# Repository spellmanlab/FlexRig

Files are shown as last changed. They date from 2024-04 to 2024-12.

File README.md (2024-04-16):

# FlexRig


FlexRig is an open-source platform for head-fixed mouse behavior. Originally designed to run an attentional set-shifting task, it can be used for a wide range of water reward-based tasks involving auditory, whisker somatosensory, and/or olfactory stimuli.

To start using FlexRig:
1. Download the repository
2. Gather the components from the parts list. This includes url-links to commercially available items, 3D-printable .stl files, CNC-machinable files, and printable PCB board design 
4. Assemble the rig, following the illustrated assembly guide
5. Install the Arduino function library

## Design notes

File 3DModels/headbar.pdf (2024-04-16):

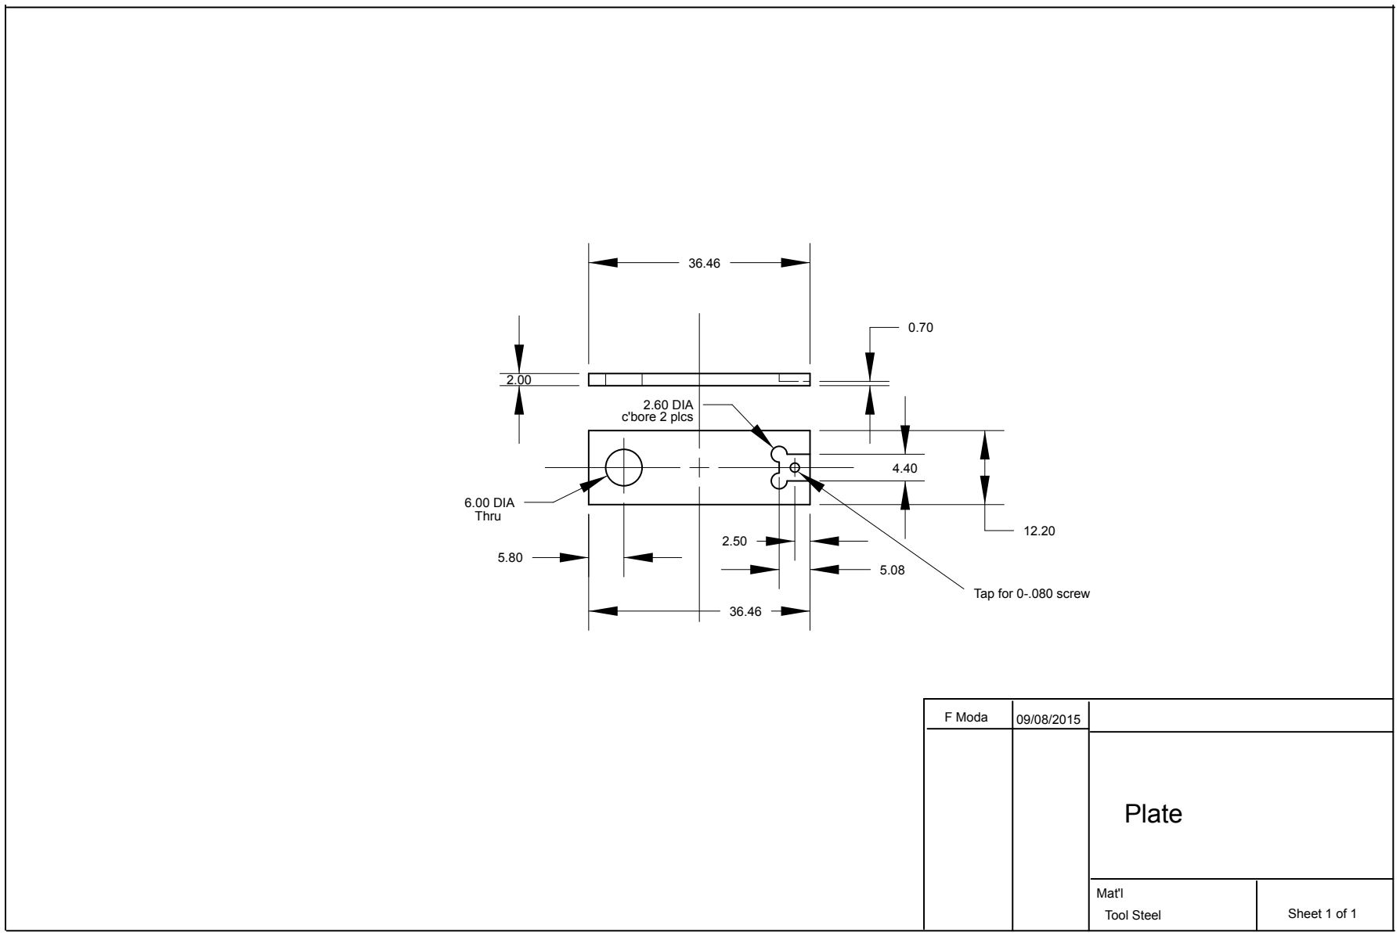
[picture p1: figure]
F Moda; Mat'l; Sheet 1 of 1; 6.00 DIA; 2.60 DIA c'bore 2 plcs; Thru; Tool Steel; Plate; Tap for 0-.080 screw

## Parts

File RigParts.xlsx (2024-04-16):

part # | component | item description | # | usage notes | part ID | supplier | link
P1 | base + head restraint | 6"x6" breadboard | 1 | platform for all components | MB6 | Thorlabs | https://www.thorlabs.com/thorproduct.cfm?partnumber=MB6
P2 |  | 3" x 1/2" posts | 2 | supports head plates | TR3 | Thorlabs | https://www.thorlabs.com/thorproduct.cfm?partnumber=TR3
P3 |  | adhesive teflon sheet, Teflon (PTFE) sheets, various sizes, 0.03" (1/32") thick, with 3M 300LSE industrial-strength self-adhesive backing [TEFLON-3M-all] | 1 | covers the base, makes for easier cleanup | 3M | 3M | https://www.amazon.com/Teflon-industrial-strength-self-adhesive-backing-TEFLON12x12-3M/dp/B00CM06JAG
P4 |  | Adapter with Internal 4-40 Threads and External 1/4"-20 Threads | 2 | mounting arduino to base | AE4E25E | Thorlabs | https://www.thorlabs.com/thorproduct.cfm?partnumber=AE4E25E#ad-image-0
P5 |  | 1/4"-20 set screw, length 0.5" | 1 | slotting treadmill front | 91375A537 | McMaster-Carr | https://www.mcmaster.com/91375A537/
P6 |  | 1/4"-20 cap screw, length 0.5-1" | 3 | slott treadmill, rear, fastening air/water holder to base | 92220A183 | McMaster-Carr | https://www.mcmaster.com/92220A183/
P7 |  | button-head screw | 1 | hold Arudino case to base | 92949A110 | McMaster-Carr | https://www.mcmaster.com/92949A110/
P8 |  | 4-40 cap screw, 1" length | 1 | hold Arduino to case and base | 91251A110 | McMaster-Carr | https://www.mcmaster.com/91251A110/
P9 |  | head bars | 2 | fastens head plate to head posts | headbar.stl |  | https://github.com/spellmanlab/FlexRig
P10 |  | Arduino Mega 2560 | 1 | control components and log behavior data | 1050-1018-ND | Digikey | https://www.digikey.com/en/products/detail/arduino/A000067/2639006
P11 | air/water control | flowmeter, Masterflex Variable-Area Flowmeter with Valve, Acrylic Housing, Brass Fitting, 50-mm; 0.5 LPM Air | 1 | regulates airflow to odorants | 2968K201 | McMaster-Carr | https://www.mcmaster.com/2968K201/
P12 |  | M5 screw | 1 | secures flow meter to holder | 92290A277 | McMaster-Carr | https://www.mcmaster.com/92290A277/
P13 |  | Luer 3-way stopcock, F/F/M | 2 | air and water intake | PVAP-MFF-PC | ISM | https://www.industrialspec.com/shop/pvap-mff-pc.html
P14 |  | Luer 3-way T splitter, F/F/M | 5 | coupled to water and odorant bottles | CFFT-WN | ISM | https://www.industrialspec.com/shop/plastic-fittings/plastic-luer-fittings/luer-to-luer-plastic-luer-fittings/cfft-series/cfft-wn.html
P15 |  | Luer 3/32" barbed connector, F | 1 | connects water bottle to water intake stopcock | CFLLA-332-N | ISM | https://www.industrialspec.com/shop/plastic-fittings/plastic-luer-fittings/luer-to-barb-plastic-luer-fittings/cfla-series/cflla-332-n.html
P16 |  | Luer 3/32" barbed connector, M | 2 | 1) connects air intake to flowmeter, 2) connects water intake to water solenoids | CIML-332EA-WN | ISM | https://www.industrialspec.com/shop/plastic-fittings/plastic-luer-fittings/luer-to-barb-plastic-luer-fittings/ciml-series/ciml-332ea-wn.html
P17 |  | Luer elbow adaptor, M-F | 3 | 1) connects water bottle to water intake, 2-3) couple to lickspout needles | CFLET-WN | ISM | https://www.industrialspec.com/shop/plastic-fittings/plastic-luer-fittings/luer-to-luer-plastic-luer-fittings/cfle-series/cflet-wn.html
P18 |  | Luer snap-on threads | 8 | secure male luer adapters to female luer adapters | CLFSR-WN | ISM | https://www.industrialspec.com/shop/plastic-fittings/plastic-luer-fittings/panel-mount-luers/clfsr-series-finger-snap-luer-lock-ring/clfsr-wn.html
P19 |  | 1/8 NPT fitting (3/32" barb) | 2 | connecting 1/16" PTFE tubing to flowmeter intake and exhaust | F325483 | ISM | https://www.industrialspec.com/shop/f325483.html
P20 |  | PTFE (Teflon) tubing, 1/16" OD, 1/32" ID | 100' | air and water lines | PTFE-132116-100 | ISM | https://www.industrialspec.com/shop/plastic-tubing/ptfe-fluoropolymer-tubing/ptfe-132116-100.html
P21 |  | Luer 3/32" barbed check valve, intake | 4 | air intake to odorant tube | BCV-67220-ML | ISM | https://www.industrialspec.com/shop/medical-products/medical-check-valves/bcv-67220-ml.html
P22 |  | Luer 3/32" barbed check valve, exhaust | 4 | air exhaust from odorant tube | BCV-67FL-220 | ISM | https://www.industrialspec.com/shop/medical-products/medical-check-valves/bcv-67fl-220.html
P23 |  | 6-40 threaded ferrules | 24 | coupling to for 1/16" OD tubing | SKU 640FF-16 | Globalfia | https://www.globalfia.com/shop/6-40-Fittings-p460224016
P24 |  | 1/4 OZ luer-capped dispensing bottles | 4 | contains odorants | JG0.25BC | Jensen Global | https://jensenglobal.com/products/0-25-ounce-cylinder-bottle-cap-kit
P25 |  | 2 OZ luer-capped dispensing bottle | 1 | contains water | JG2.0BC Bl2 | Jensen Global | https://jensenglobal.com/collections/boston-round-bottle-and-cap/products/boston-round-bottles-caps-1-2-ounces
P26 |  | Silicon tubing, 1/32" I.D., 5/32" O.D. | 10' | coupling 1/16" PTFE tubing to barbs | 57286 | US Plastics | https://www.usplastic.com/catalog/item.aspx?itemid=31559&v1=&v7=&gad_source=1
P27 |  | Silicon tubing, 1/16" I.D., 1/8" O.D. |  | coupling 1/16" PTFE tubing to male Luer connectors at odorant bottles | 57287 | US Plastics | https://www.usplastic.com/catalog/item.aspx?itemid=31560&clickid=related-slider
P28 |  | air/water holder | 1 | holds flowmeter, water bottle, odorant bottles and luer connectors | airWaterHolder.stl |  | https://github.com/spellmanlab/FlexRig
P29 |  | odorant manifold | 1 | merges odorant exhaust channels | threadedManifold.emsx |  | https://github.com/spellmanlab/FlexRig
P30 | lick stage | gavage needle, 20g | 2 |  | AFN2025S | GavageNeedle | https://gavageneedle.com/products/reusable-oral-gavage-needle?variant=865840675
P31 |  | translating post | 1 | hold lick ports | BTP2.0 (https://www.newport.com/p/BTP2.0) | Newport | https://www.newport.com/f/0.5-in.-translating-optical-posts
P32 |  | xy translating stage | 1 | hold lick ports | M-MT-XY | Newport | https://www.newport.com/p/M-MT-XY
P33 |  | 6-40 machine | 2 | hold odorant tube | 94812A663 | McMaster-Carr | https://www.mcmaster.com/94812A663/
P34 |  | 6-40 threaded ferrules | 1 | coupling to for 1/16" OD tubing | SKU 640FF-16 | Globalfia | https://www.globalfia.com/shop/6-40-Fittings-p460224016
P35 |  | plastic 8/32" thumb screw | 1 | securing lickspouts to holder | 94320A393 | McMaster-Carr | https://www.mcmaster.com/94320A393/
P36 |  | 2-56" x 5/8" screw | 1 | securing translating post to holder | 91802A083 | McMaster-Carr | https://www.mcmaster.com/91802A083/
P37 |  | 2-56 nut | 1 | securing translating post to holder | 90480A003 | McMaster-Carr | https://www.mcmaster.com/90480A003/
P38 |  | lickspout holder | 1 | securing lickspouts to xy stage and base | lickSpoutPostHolder.stl |  | https://github.com/spellmanlab/FlexRig
P39 |  | 8-32 cap screw, 1/4" length | 3 | 1) fastening lickspout holder to XY stage, 2) fastening head bars to posts | 90128A191 | McMaster-Carr | https://www.mcmaster.com/90128A191/
P40 | treadmill | toy tank treads | 76 links | supports mouse, facilitates running, conducts lick detection current | TT35056 | Warp United | https://www.amazon.com/Assembled-Workable-T-34-76-T-34-85-Self-propelled/dp/B07Q9QJSNC
P41 |  | steel bearings | 6 | treadmill axle bearings | 7804K143 | McMaster-Carr | https://www.mcmaster.com/7804K143/
P42 |  | 2" mini posts | 2 | treadmill axles | MS2R | Thorlabs | https://www.thorlabs.com/thorproduct.cfm?partnumber=MS2R
P43 |  | 4-40 screws and washers | 1 kit | securing bearings to treadmill frame | ALAST0440 | Fastener Express | https://www.fastener-express.com/4-40-alloy-stainless-asortment.aspx
P44 |  | rotary encoder | 1 | measure running speed | AMT103-V | Digi-key | https://www.digikey.com/en/products/detail/cui-devices/AMT103-V/827016?s=N4IgTCBcDaIIIFkAqBGADAZgLQDUQF0BfIA
P45 |  | 1/4-20 cap screws, 1/2" | 4 | secure treadmill to breadboard | 92220A183 | McMaster-Carr | https://www.mcmaster.com/92220A183/
P46 |  | 3mm banana plug | 1 | 3.3v lick detection voltage connector (post to mouse platform) | generic | Amazon | https://www.amazon.com/LinsyRC-Gold-Plated-Connector-Adapter-Battery/dp/B08H8MY431
P47 |  | mouse platform | 1 | supports mouse/treadmill | treadmillBase.stl |  | https://github.com/spellmanlab/FlexRig
P48 |  | treadmill sprockets (aluminum) | 2 | holds treads | treadmillSprockets.stl |  | https://github.com/spellmanlab/FlexRig
P49 | command stage | 2-way solenoid valves, 12v, face-mounted | 2 | solenoid valves for dispensing water reward | LHDB1252115H | The Lee Company | https://www.theleeco.com/resources/files/2-port-hdi-solenoid-valve-pds-124-2014-12/
P50 |  | 3-way solenoid valves, 12v, face-mounted | 4 | route air to one of the four odorant tubes or bypass all four | LHDA1221411H | The Lee Company | https://www.theleeco.com/products/electro-fluidic-systems/solenoid-valves/control-valves/lhd-series/3-port/face-mount/
P51 |  | air/water face-mount manifold (aluminum) | 1 | mount solenoids to tubing | threadedFaceMount.emsx |  | https://github.com/spellmanlab/FlexRig
P52 |  | solenoid retention brackets | 3 | attaches selonoids to face mount manifolds (optional) | LLWX0307130A | The Lee Company | https://www.theleeco.com/products/electro-fluidic-systems/solenoid-valves/control-valves/general-accessories-replacement-parts/
P53 |  | 2-56 solenoid retention screws, 0.5" length | 8 | fasten solenoids to face mount | 91251A081 | McMaster-Carr | https://www.mcmaster.com/91251A081/
P54 |  | DF Robot DF Player Pro | 1 | sound card | 1738-DFR0768-ND | Digikey | https://www.digikey.com/en/products/detail/dfrobot/DFR0768/13978502
P55 |  | H-bridge | 2 | 4-40 cap screw, 1" length |  |  | https://www.digikey.com/en/products/detail/texas-instruments/SN754410NE/380180?gad_source=1
P56 |  | 6-pin screw terminal, 2.54mm pitch | 2 | connecting wires to PCB board | A98337-ND | Digikey | https://www.digikey.com/en/products/detail/te-connectivity-amp-connectors/282834-6/1153267?gad_source=1
P57 |  | 2-pin screw terminal, 2.54mm pitch | 1 | connecting linear actuator to PCB board | A98333-ND | Digikey | https://www.digikey.com/en/products/detail/te-connectivity-amp-connectors/282834-2/1150135?gad_source=1
P58 |  | 8-pin male header | 6 | connecting PCB board to arduino | 732-5321-ND | Digikey | https://www.digikey.sk/en/products/detail/w%C3%BCrth-elektronik/61300811121/4846839
P59 |  | 2-pin female header | 6 | connecting solenoids to board | 2057-RS1-02-G-ND | Digikey | https://www.digikey.com/en/products/detail/adam-tech/RS1-02-G/9832044
P60 |  | 6-pin female header | 2 | connecting sound board to main board | 2057-RS1-06-G-ND | Digikey | https://www.digikey.com/en/products/detail/adam-tech/RS1-06-G/9832050
P61 |  | 2x18 pin stackable female header | 1 | connecting PCB board to Arduino | SSW-118-03-G-D-ND | Digikey | https://www.digikey.com/en/products/detail/samtec-inc./SSW-118-03-G-D/7880952?gad_source=1
P62 |  | 1MOhm resistors | 11 | Dropping current | CF14JT1M00TR-ND | Digikey | https://www.digikey.com/en/products/detail/stackpole-electronics-inc/CF14JT1M00/1741316
P63 |  | ribbon cable | 1' | connection from PCB board to speakers, lick detectors, mouse platform | 3M157841-1-ND | Digikey | https://www.digikey.com/en/products/detail/3m/3302%2F26%2520100/9478439
P64 |  | PCB board | 1 | connects arduino to peripheral components | FlexRigShield.fzz |  | https://aisler.net/p/KLVRBWII
P65 | vibration stage | speakers (Tymphany, 20Hz-20kHz) | 2 | auditory and whisker stimuli | HPD-50N25PR00-32-ND | Digikey | https://www.digikey.com/en/products/detail/peerless-by-tymphany/HPD-50N25PR00-32/6211129
P66 |  | Locking Ball and Socket Mount | 2 | mounting speakers to platform | TRB1 | Thorlabs | https://www.thorlabs.com/thorproduct.cfm?partnumber=TRB1
P67 |  | Lens Mount with Retaining Ring for Ø2" Optics | 2 | mounting speakers to platform | LMR2 | Thorlabs | https://www.thorlabs.com/thorproduct.cfm?partnumber=LMR2#ad-image-0
P68 |  | Adapter 8-32 Threads and 1/4"-20 Threads | 2 | mounting speakers to platform | AP8E25E | Thorlabs | https://www.thorlabs.com/thorproduct.cfm?partnumber=AP8E25E
P69 |  | 2-pin screw terminal, 2.54mm pitch | 2 | connecting linear actuator to PCB board | PRT-10571 | Sparkfun.com | https://www.sparkfun.com/products/10571
P70 |  | speaker funnels | 2 | condensing sound wave, directing toward whisker vibrissae | speakerfunnel.stl |  | https://github.com/spellmanlab/FlexRig
 |  | 1/16" OD PTFE tubing cuts:
 |  | 8" (4x) | odorant tubes to manifold, outflow luer valve one side, 6-40 ferrule on the other
 |  | 10" (4x) | solenoids to odorant tubes, inflow luer valve one side, 6-40 ferrule on the other
 |  | 7" (1x) | clean air solenoid to manifold, 6-40 ferrules both sides
 |  | 1" (3x) | solenoid-to-solenoid, 6-40 ferrules both sides
 |  | 12" (1x) | water, stopcock to solenoid, 6-40 ferrule one side, male luer barb on the other
 |  | 6" (2x) | water, solenoids to lick spouts, 6-40 ferrule one side, male luer bard on the other
 |  | 12" (1x) | water bottle to stopcock, female luer barb one side, other side bare
 |  | 4" (1x) | air stopcock to flow regulator, NPT barb one side, male luer barb on the other
 |  | 12" (1x) | flow regulator to solenoid, NPT barb one side, 6-40 ferrule on the other

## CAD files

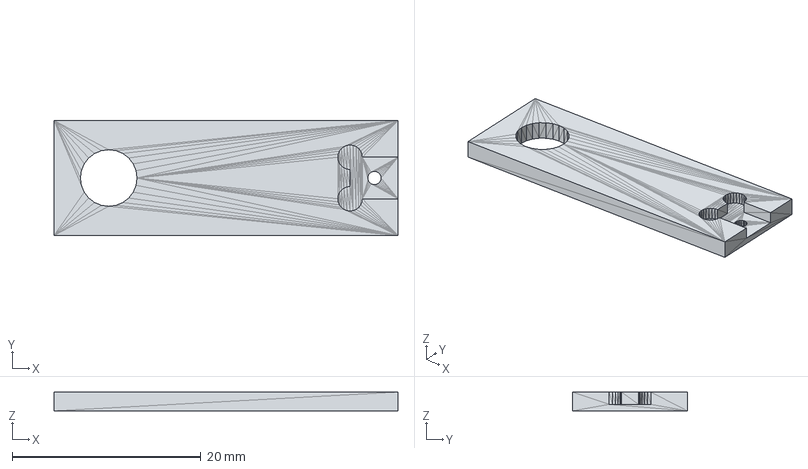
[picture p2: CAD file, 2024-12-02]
3DModels/headbar.step
36.5 x 12.2 x 2.00 mm

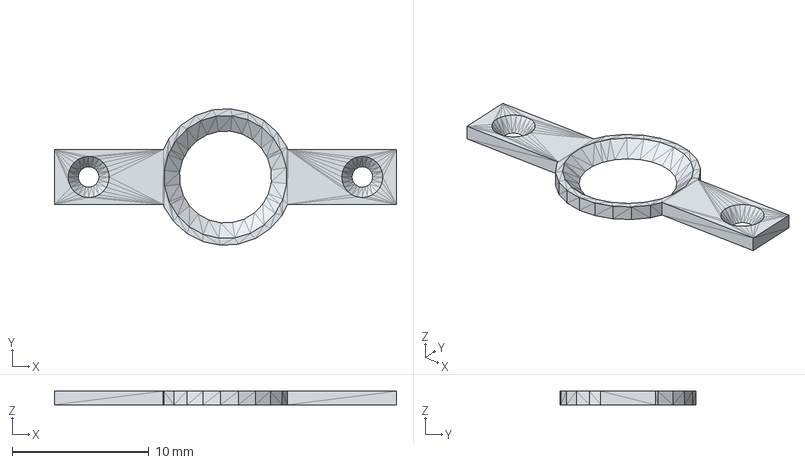
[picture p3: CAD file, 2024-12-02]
3DModels/headplate.step
25.0 x 9.97 x 1 mm

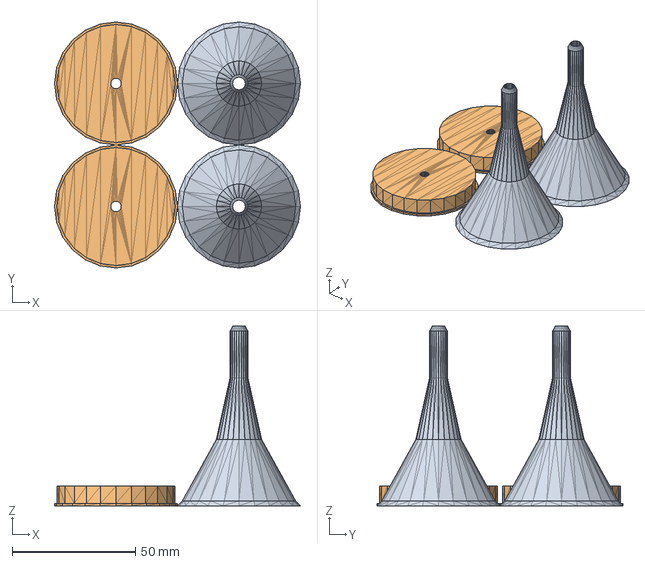
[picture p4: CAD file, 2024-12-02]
3DModels/speakerFunnel.step
100.0 x 100.0 x 73.0 mm

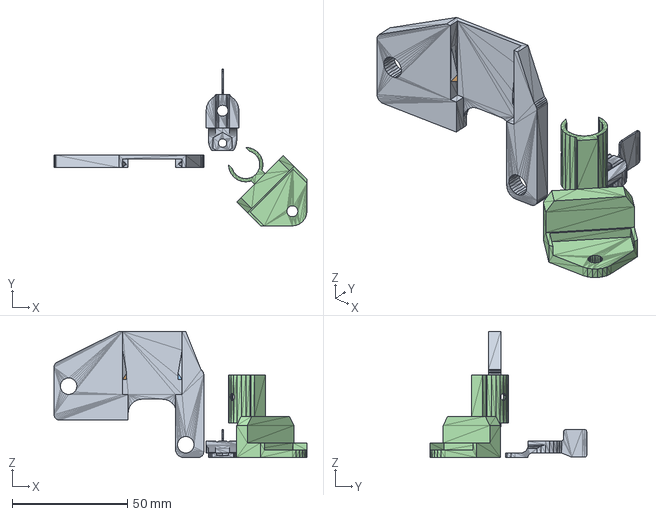
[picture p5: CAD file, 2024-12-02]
3DModels/lickSpoutPostHolder.step
109.7 x 68.0 x 54.7 mm

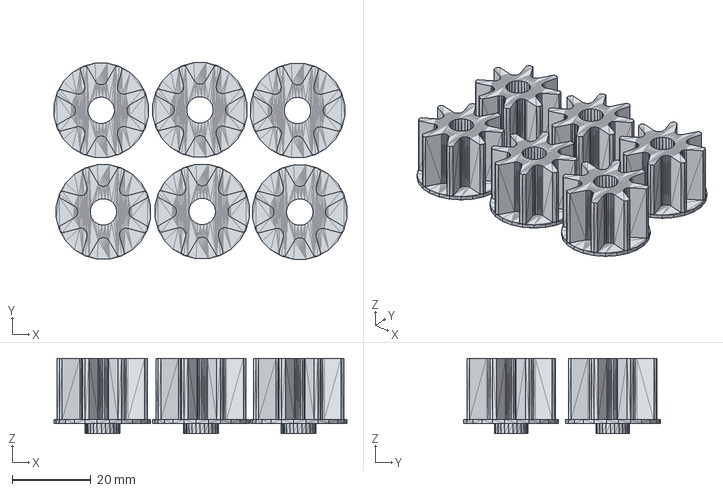
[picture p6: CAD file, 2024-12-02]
3DModels/treadmillSprockets.step
74.3 x 49.9 x 19.1 mm

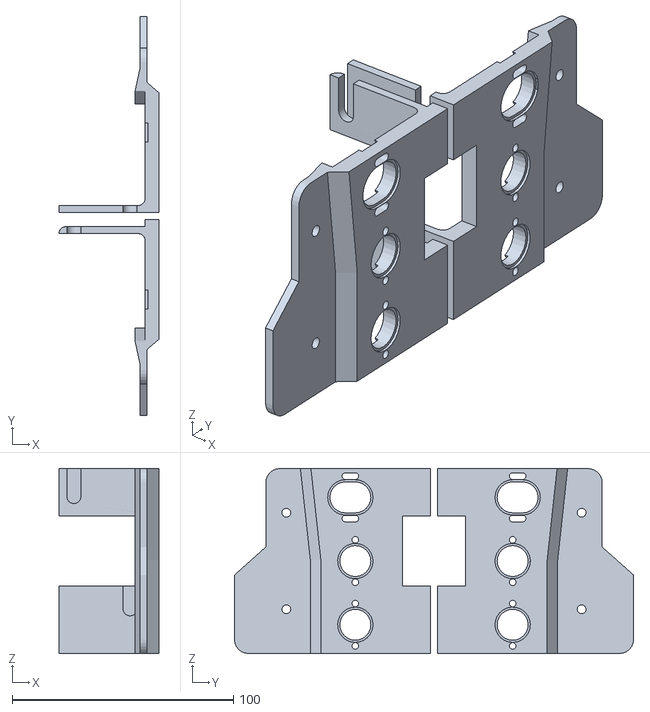
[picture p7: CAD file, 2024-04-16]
3DModels/treadmillBase.stl
45.4 x 180.6 x 83.7

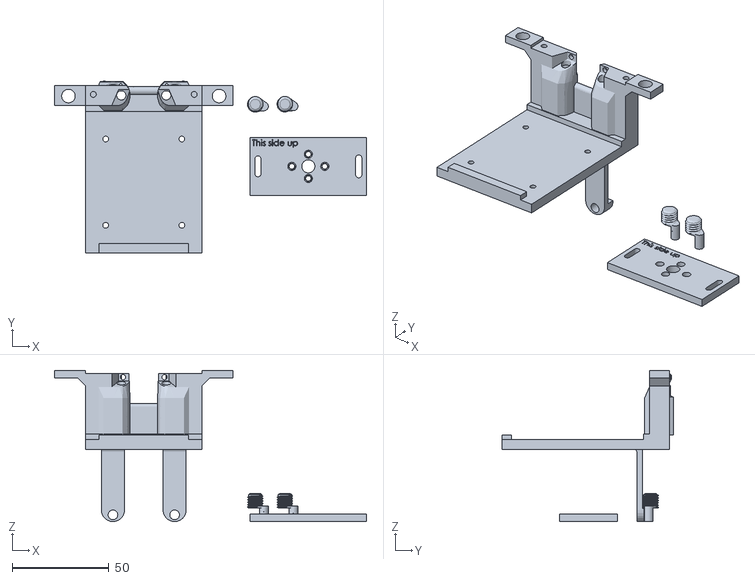
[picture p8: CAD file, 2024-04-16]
3DModels/SIR_Headport13.stl
160.9 x 88.7 x 78.0

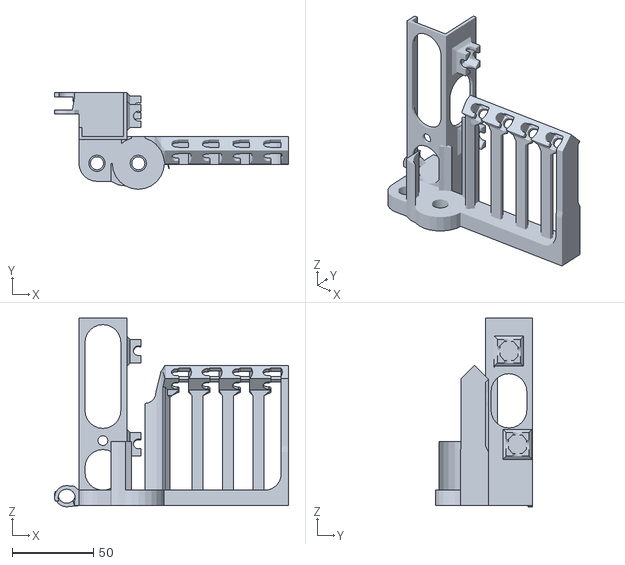
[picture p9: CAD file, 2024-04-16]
3DModels/airWaterHolder.stl
143.8 x 59.4 x 116.0

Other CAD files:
3DModels/headbar.stl
3DModels/headplate.stl
3DModels/lickSpoutPostHolder.stl
3DModels/speakerFunnel.stl
3DModels/treadmillSprockets.stl

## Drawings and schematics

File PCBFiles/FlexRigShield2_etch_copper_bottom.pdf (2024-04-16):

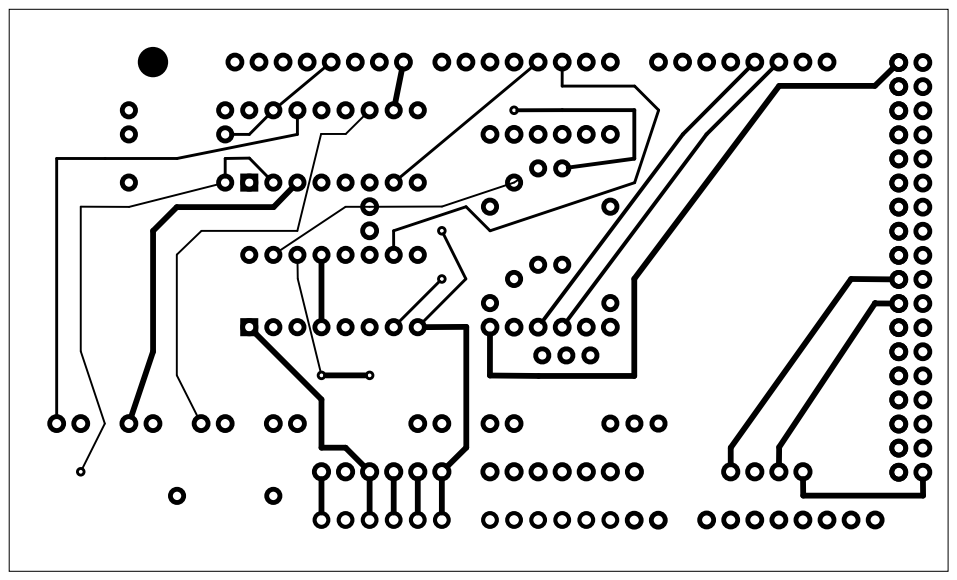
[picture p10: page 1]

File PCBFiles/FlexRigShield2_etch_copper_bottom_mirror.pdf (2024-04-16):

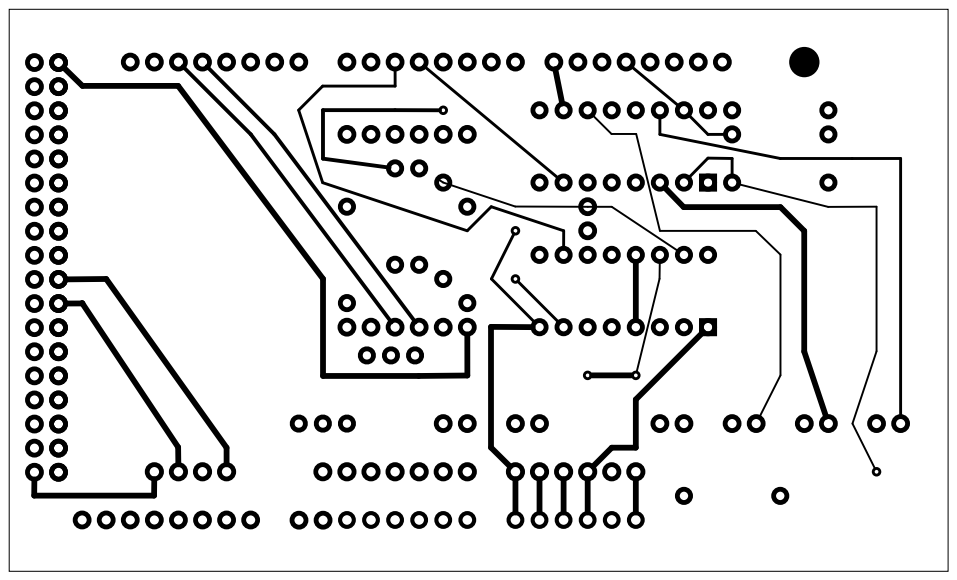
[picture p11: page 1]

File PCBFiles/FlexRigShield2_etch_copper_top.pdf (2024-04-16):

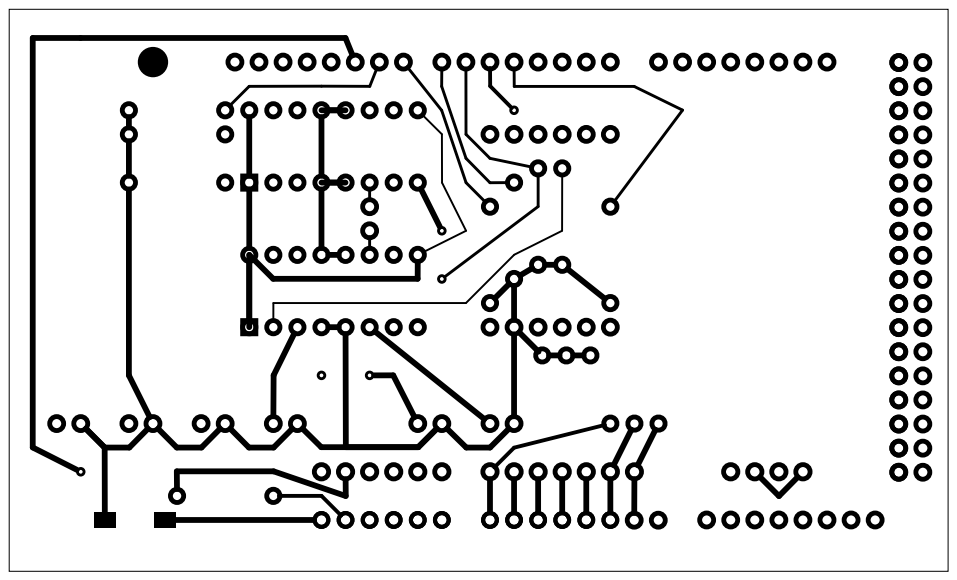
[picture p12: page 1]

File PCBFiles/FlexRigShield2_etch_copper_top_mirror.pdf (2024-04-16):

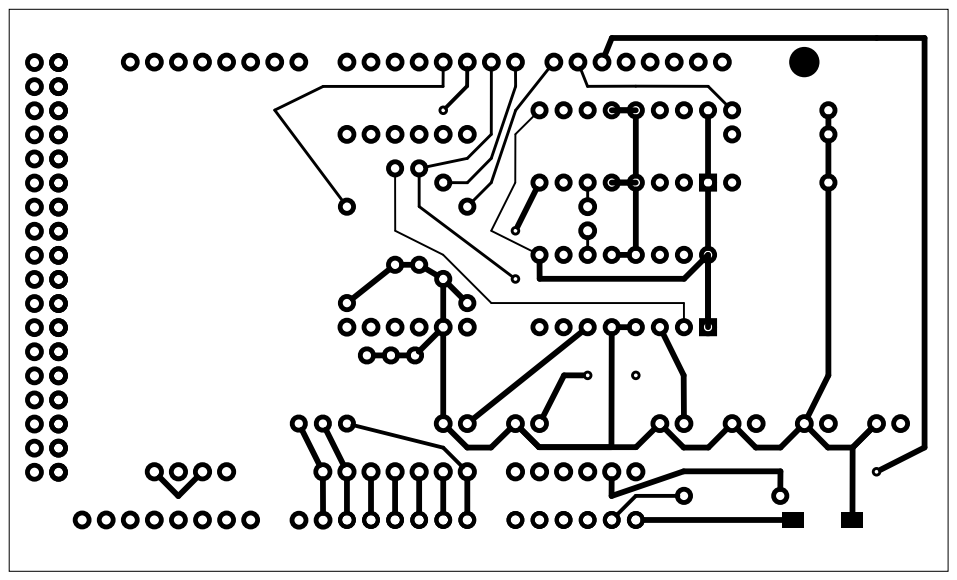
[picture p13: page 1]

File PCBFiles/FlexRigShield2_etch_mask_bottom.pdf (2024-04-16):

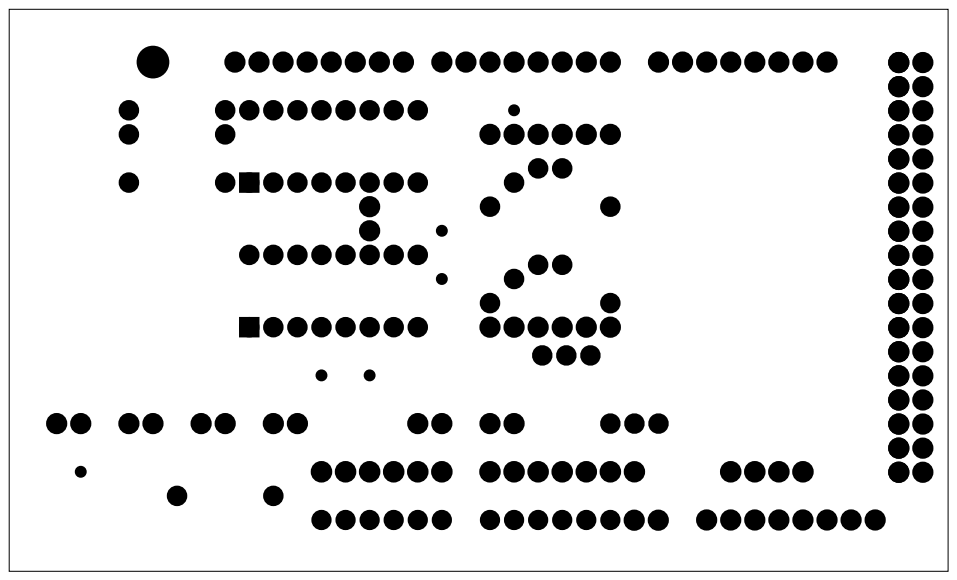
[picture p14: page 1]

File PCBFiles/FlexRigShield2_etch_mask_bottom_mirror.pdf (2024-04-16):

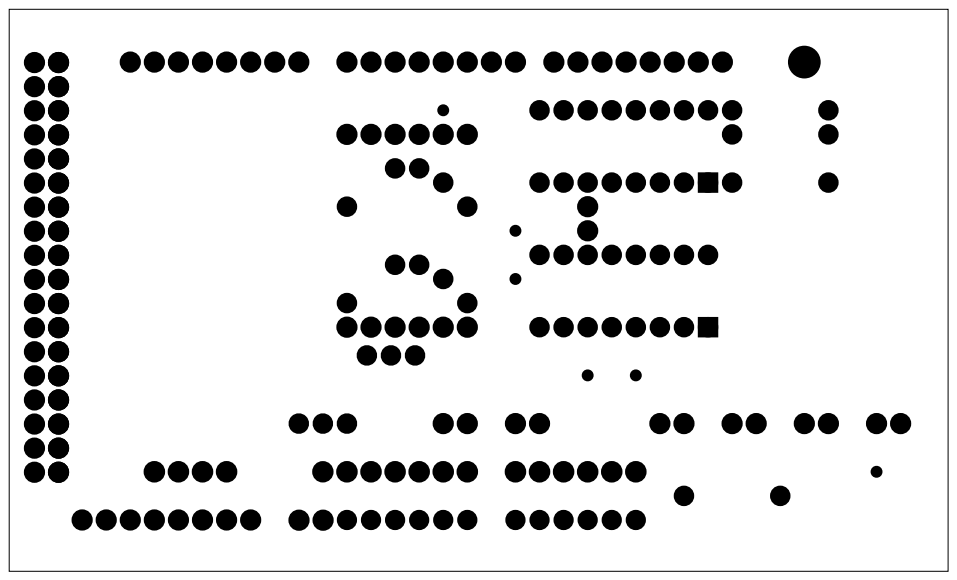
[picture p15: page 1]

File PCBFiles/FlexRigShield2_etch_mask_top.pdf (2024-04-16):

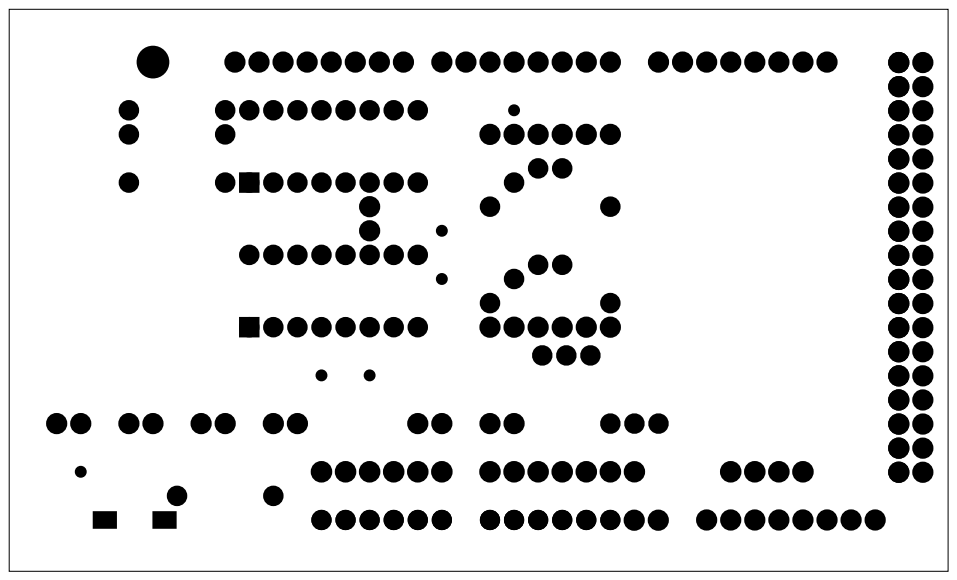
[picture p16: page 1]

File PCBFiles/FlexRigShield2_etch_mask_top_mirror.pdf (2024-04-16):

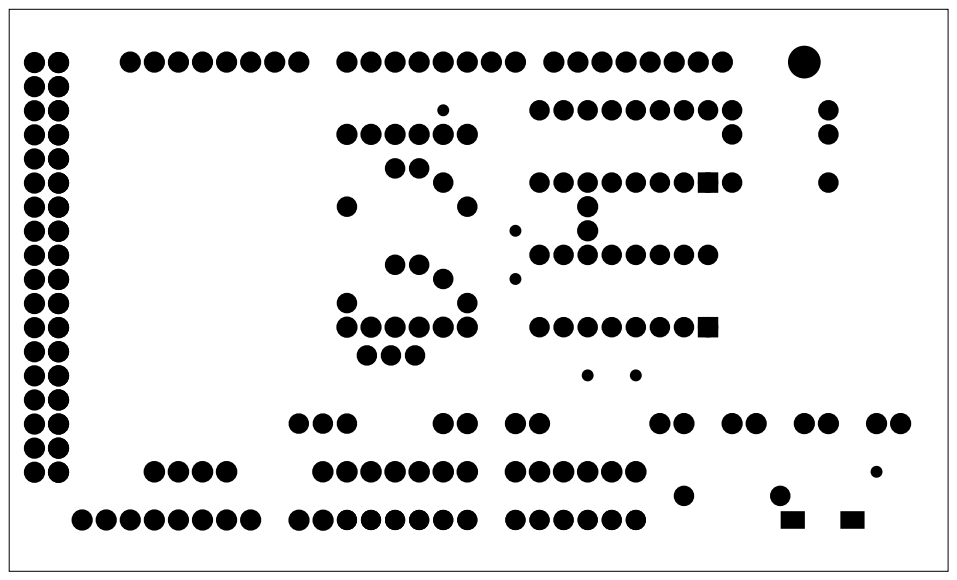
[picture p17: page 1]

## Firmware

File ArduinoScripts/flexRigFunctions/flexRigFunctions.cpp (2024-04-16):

//NOTE: the following third party libraries are required: elapsedMillis, Average, DFRobot_DF1201S
#include <elapsedMillis.h>
    elapsedMillis timeElapsed_lib;
#include <Average.h>
#include <TimerOne.h>
#include <TimerThree.h>
#include <DFRobot_DF1201S.h>
    DFRobot_DF1201S DF1201S;

int solenoidOpenTime = 25;             //open time on water solenoid, in ms (~25ms @ ~3psi = ~4uL)
float lickThresh = 20;                 //threshold voltage difference for lick detection
int H2OVol = 4;			//amount of water dispensed each time (uL)
int lickPrev=0;
int lickedL=0;                        
int lickedR=0;
int lickNumL=0;
int lickNumR=0;
int RT=0;

int LEDChannel = 40;
int optoChannel = 38;
int ledState = LOW;
int H2OL = 7;
int H2OR = 6;
int odorAirSupply = 5;
int odorPair = 10;
int odorAB = 11;
int odorCD = 8;
int rewardOut = 46;
int lickingLOut = 48;
int lickingROut = 49;



void initializeBoard(){
    Serial.begin(9600);
    Serial1.begin(115200);
    delay(100);
    for (int i=0; i<=53; i++){  
      pinMode(i, OUTPUT);
      digitalWrite(i, LOW);
    }
      while(!DF1201S.begin(Serial1)){
        Serial.println("Init failed, please check the wire connection!");
        delay(1000);
      }
      DF1201S.setPrompt(false);
      DF1201S.setLED(false);
      DF1201S.setVol(/*VOL = */19); //Sets audio card volume 20 max.
      DF1201S.switchFunction(DF1201S.MUSIC); //This command makes the speakers say "Music"
      DF1201S.setPlayMode(DF1201S.SINGLE); //Makes it so the player will stop if it reaches the end of a file
}


void dispense(int lickSpout = 0){
  if (lickSpout != 0) {
	if(lickSpout == -1){
	  digitalWrite(H2OL,HIGH);
	  digitalWrite(rewardOut,HIGH);
    	  delay(solenoidOpenTime);
    	  digitalWrite(H2OL,LOW);
	  digitalWrite(rewardOut,LOW);
	}
	else{
	  digitalWrite(H2OR,HIGH);
	  digitalWrite(rewardOut,HIGH);
    	  delay(solenoidOpenTime);
   	  digitalWrite(H2OR,LOW);
	  digitalWrite(rewardOut,LOW);
	}
  }
  else {
    digitalWrite(H2OL,HIGH);
    digitalWrite(H2OR,HIGH);
    digitalWrite(rewardOut,HIGH);
    delay(solenoidOpenTime);
    digitalWrite(H2OL,LOW);
    digitalWrite(H2OR,LOW);
    digitalWrite(rewardOut,LOW);
  }
}



void playTone(int tone_num, int tone_length = -1){
  DF1201S.playFileNum(tone_num);
  DF1201S.setPlayTime(/*Play Time = */0);
  if(tone_length!=-1){
    delay(tone_length);
    DF1201S.setPlayTime(/*Play Time = */3);     //kill tone by advancing to the end of the file
  };
};



void killTone(){
  DF1201S.setPlayTime(/*Play Time = */3);       //kill tone by advancing to the end of the file
};



void lickDetect(int lickData[], int lickSpout, int lickExit = 0, int detectDur = 300000) {
      //input arguments:
      //1) lickData (lickedL, lickedR, lickNumL, lickNumR, RT)
      //2) lickspout (-1=left, 1=right, 0=both)
      //3) lickExit (whether a lick terminates the function; 0=no, 1=yes)
      //4)duration of lick detection in ms
      //returns the array lickData:
      //1) lickedL (0/1)
      //2) lickedR (0/1)
      //3) lickNumL (number of left licks, when lickExit !=0)
      //4) lickNumR (number of right licks, when lickExit !=0)
      //5) RT (reaction time; latency to first lick)
      Average<float> lickAveR(3);
      Average<float> lickAveL(3);   
      lickedL=0;
      lickedR=0;
      lickNumL=0;
      lickNumR=0;
      lickPrev=0;
      RT=0;
      timeElapsed_lib=0;
      int exit=0;
      while (exit == 0 && timeElapsed_lib <= detectDur) {
        lickAveR.push(analogRead(A5) - analogRead(A0));
        lickAveL.push(analogRead(A0) - analogRead(A5));
        if (lickSpout != -1 && lickAveR.minimum() > lickThresh) {
          lickedR = 1;
          RT = timeElapsed_lib;
          digitalWrite(lickingROut, HIGH);
          delay(5);
          digitalWrite(lickingROut, LOW);
	  if(lickExit==1){exit=1;}
        }
        if (lickSpout != 1 && lickAveL.minimum() > lickThresh) {
          lickedL = 1;
          RT = timeElapsed_lib;
          digitalWrite(lickingLOut, HIGH);
          delay(5);
          digitalWrite(lickingLOut, LOW);
	  if(lickExit==1){exit=1;}
        }

        if (lickPrev == 0 && lickedR == 1) {
          lickNumR = lickNumR + 1;
        }
        if (lickPrev == 0 && lickedL == 1) {
          lickNumL = lickNumL + 1;
        }
        if (lickedR == 1 || lickedL == 1) {
           lickPrev = 1;
        }
        else {
          lickPrev = 0;
        }
	lickedL = 0;
	lickedR = 0;
        delay(5);
      }
	if(lickNumL>0){lickedL=1;}
	if(lickNumR>0){lickedR=1;}
    lickData[0] = lickedL;
    lickData[1] = lickedR;
    lickData[2] = lickNumL;
    lickData[3] = lickNumR;
    lickData[4] = RT;
	return lickData;
}



void presentOdorant(int odorant, int odorDur = -1){
  digitalWrite(odorAirSupply, HIGH);
  
  if(odorant == 2){
    digitalWrite(odorAB,HIGH);
  }
  if(odorant == 3){
    digitalWrite(odorPair,HIGH);
  }
  if(odorant == 4){
    digitalWrite(odorPair,HIGH);
    digitalWrite(odorCD,HIGH);
  }

  if(odorDur != -1){
    delay(odorDur);
      digitalWrite(odorAirSupply,LOW);
      digitalWrite(odorPair,LOW);
      digitalWrite(odorAB,LOW);
      digitalWrite(odorCD,LOW);
  }
}



void killOdorants(){
  digitalWrite(odorAirSupply,LOW);
  digitalWrite(odorPair,LOW);
  digitalWrite(odorAB,LOW);
  digitalWrite(odorCD,LOW);
}



void blinkLED(){
  if(ledState==LOW){ledState=HIGH;}
  else{ledState=LOW;}
  digitalWrite(optoChannel,ledState); 
}

void timerKill(){
  Timer1.detachInterrupt();
  digitalWrite(optoChannel,LOW);
  ledState=LOW;
}

void photoStim(float freq, float dur){
	//freq = frequency (Hz); 0 = constant illumination
	//dur = duration (ms)
	ledState==LOW;
	if(freq==0){digitalWrite(optoChannel,HIGH);}
	else{ 
	  Timer3.attachInterrupt(timerKill);
	  Timer3.initialize(dur*1000);
	  Timer3.restart();
	  delay(1);
	  Timer1.attachInterrupt(blinkLED);	  
	  Timer1.initialize((1000/freq)/2*1000);
	  Timer1.restart();
	  
	}
}
